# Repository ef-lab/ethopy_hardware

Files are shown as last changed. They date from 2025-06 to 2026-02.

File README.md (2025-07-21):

# 🏠 Hardware for EthoPy

Welcome to the **Hardware for EthoPy** repository! This collection includes all hardware information required to build the setups described in EthoPy. 

## 📦 What's Inside

This repo includes one folder for each behavioral system supported by EthoPy with the:
- **Instructions** – step-by-step guides to build this setup and parts list 
<!-- - **Parts list** – all hardware components required -->
- **3d_designs** – ready-to-print `.stl` files 

## 📁 File Structure

```bash
├── README.md
├── Homecage/
│   └── README.md
│   └── Instructions.pdf
│   └── 3d_designs      
│       └── base.stl
│       └── screen_holder.stl
│       └── ...
├── Openfield/
│   └── ...
├── Air-track/
│   └── ...
```

<!-- ## 📸 Gallery

_Add screenshots or photos of the final printed setup here!_ -->

## 🛠️ Modifications & Contributions

Want to tweak a design? Feel free to fork the repo and customize. PRs are welcome if you want to contribute new variations or improvements!

## 📜 License

This project is licensed under the **MIT License** – see the [LICENSE](./LICENSE) file for details.

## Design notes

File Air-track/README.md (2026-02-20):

# Air-track setup

In this paradigm, head-fixed mice perform a visual two-alternative forced choice task. This setup can be adapted to accommodate more sensory modalities by using appropriate equipment.

<p align="center">
  
</p>

## Hardware Parts List

### Electronics

| # | Item | Qty | Source | Identifier | Ind. Price | Notes |
|:-:|:-:|:-:|:-:|:-:|:-:|:-:|

| 1 | Bpod port interface board | 3 | Sanworks | 1008 | 33€ |Controlling the behavior ports | 

| 2 | solenoid valves | 2 | LEE | LHDA0533415H | 92.81€ | |

| 3 | Infrared Emitter 880nm Circular Right Angle 2-Pin Side Looker | 3 | Honeywell | SEP8736-002 | 4.75€ |For the behavior ports |

| 4 | Phototransistor IR Chip Silicon 880nm 2-Pin Side Looker | 3 | Honeywell | SDP8436-002 | 1,31€ | For the behavior ports |

| 5 | Ethernet cable | 3 | Bel | BC-5UK005F | 2.74 € | |

| 6 | Cable 0.05 mm², Ø 0.8mm | 1 | TRU_ | 1567774 | 4.29€ | |

### Other Hardware

| # | Item | Qty | Source | Identifier |  Ind. Price | Notes |
|:-:|:-:|:-:|:-:|:-:|:-:|:-:|

| 1 | Plexiglas air-table | 1 | Provided by Mostafa A. Nashaat, Larkum Lab, Larkum Lab, Charite, Berlin | | | |

| 2 | PLA platform | 1 | Provided by Mostafa A. Nashaat, Larkum Lab, Charite, Berlin | | | |

| 3 | Behavior port | 3 | Sanworks |  | 215€ |

| 4 | Crimp For Dupont Female | 15 | Local Market |  | 0.50€ | |

| 5 | Tygon S3™ E-3603 Tubing (water) Ø Inner 2.38mm, Ø outer 3.97mm | 4 pieces | Optubus | TY2,38ST3,97 | 1,89€/m | |

| 6 | Tygon S3™ E-3603 Tubing (water) Ø Inner 0.79mm, Ø outer 2.38mm | 2 pieces | Optubus | TY0,79ST2,38 | 1,46€ /m | |

| 7 | V-Hive Enclosure Base Model | 1 | RatRig | HW3303GK | 118€ | |

| 8 | Sound insulator ISOLFON foam plate | 4 pieces 50x50cm and 2 pieces 50x43cm | Local Market | | ~3.5€ / 5 sq. m | for sound and light insulation | 

| 9 | Heat shrink set | | GROBOTRONICS | 05-00017098 | 9.90€ | |

### 3D printed parts

You will find the blueprints for the items you should 3D print [here](3d_designs).

| # | Item | Qty | Filename |
|:-:|:-:|:-:|:-:|
| 1 | screen holders | 2 | [screen_holder.stl](3d_designs/screen_holder.stl) |

## Step-by-step Assembly instructions

You will find the blueprints for the items you should 3D print [here](3d_designs).

> **Info:** The  air-table ([see Other Hardware, part #1](#hardware1)) and platform ([see Other Hardware, part #2](#hardware2)) of the air-track were developed by Dr. Mostafa A. Nashat and assembly (https://doi.org/10.1152/jn.00088.2016, https://doi.org/10.1101/2024.08.22.608577).

**Step 1**. Set up the [Raspberry Pi Behavioral Setup](../Homecage/README.md) following steps 1-7, modifying Raspberry Pi Behavioral Setup Step 5 to connect only the valves ([see Electronics, part #2](#electro2)) to the EthoPy Controller Board.

**Step 2**. Mount the Raspberry Pi Behavioral Setup on the screen holders ([see 3D printed parts, part #1](#printed1)) in front of the air-table (Fig. 1).

<p align="center">
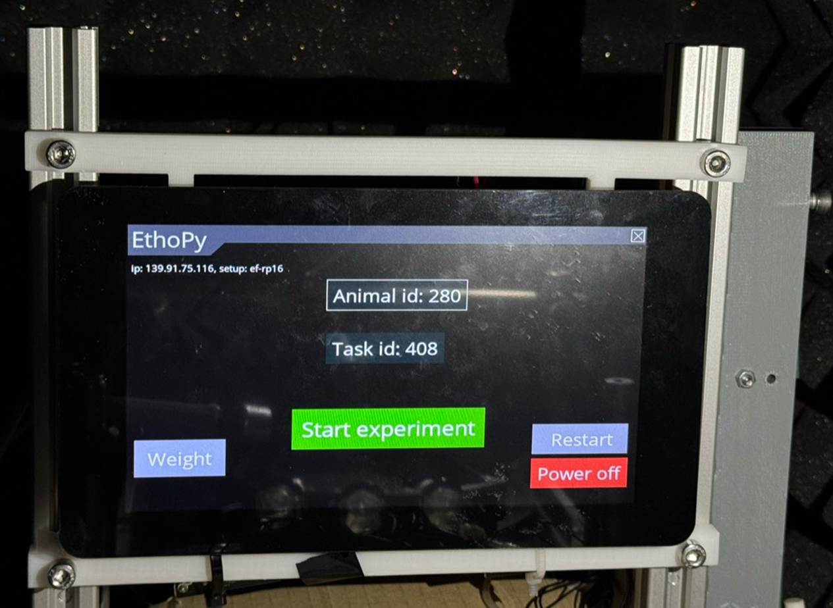
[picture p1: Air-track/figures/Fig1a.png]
  
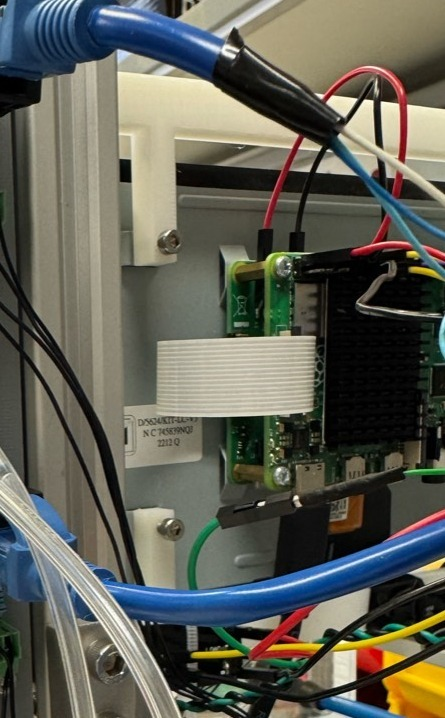
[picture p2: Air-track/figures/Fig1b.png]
  
  <br>
  <em>Figure 1: The RP behavioral setup, mounted on the aluminum rails of the air-table using the screen holders.</em>
</p>

**Step 3**. Assembling of a behavior port ([see Other Hardware, part #3](#hardware3)). Mounting of the infrared emitter ([see Electronics, part #3](#electro3)) and phototransistor ([see Electronics, part #4](#electro4)) to the port was performed following the instructions provided [here](https://sanworks.github.io/Bpod_Wiki/assembly/mouse-behavior-port-assembly/). Each platform included three behavior ports.

> **Note:** For our experiments, we did not include LED light in the behavior ports.

**Step 4**. Set up three Bpod port interface boards ([see Electronics, part #1](#electro1)) as per instructions provided [here](https://sanworks.github.io/Bpod_Wiki/assembly/port-breakout-board-assembly/). Place the Bpod port Interface Boards close to the Air-track and the Raspberry Pi Behavioral Setup for convenience.

**Step  5**. For each port, connect the infrared emitter and phototransistor with the Bpod port interface board.

> **Note:** To reduce the tension caused to the platform from these connections, prefer using wires with a cross-section of 0.05 mm² and an outer diameter of 0.8 mm ([see Electronics, part #6](#electro6)).

**Step 6**. Connecting the Bpod port interface boards to the Raspberry Pi Behavioral Setup. As the connections with the Bpod port interface board are through an Ethernet cable, you will need 3 Ethernet cables, one per port ([see Electronics, part #5](#electro5)).

**Step 7**. Remove the insulation from the edge of the Ethernet wires. Place 13 female terminals ([see Other Hardware, part #4](#hardware4)) at the end of each wire and cover the exposed terminal with insulation (e.g., heat shrink tube, [see Other Hardware, part #9](#hardware9)). In the following steps, the identification of the Ethernet cable wires is shown in (Fig. 2).

<p align="center">
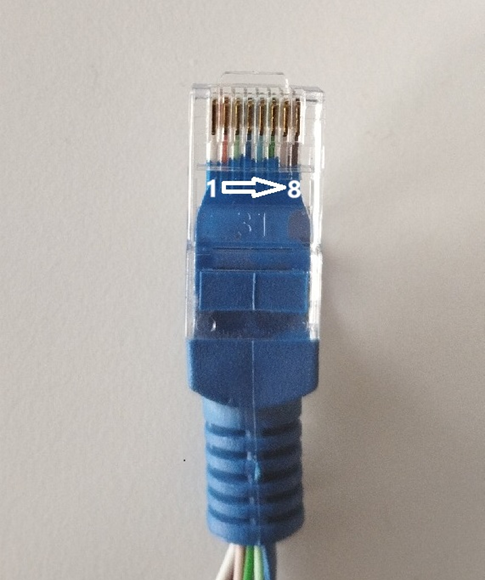
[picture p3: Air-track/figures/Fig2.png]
  
  <br>
  <em>Figure 2: Ethernet cable wire number ids.</em>
</p>

> **Note:** You will use the wires 1 (signal of the sensor), 4 (power of the emitter), 5 (ground).

**Step 8**.  The wires from the Ethernet cables are connected to the Raspberry Pi Behavioral Setup (see GPIO connections as set in [EthoPy documentation](https://ef-lab.github.io/ethopy_package/local_conf/?h=channel#4-schema-names-optional)) as follows:

- Connect `wire 1` (signal) of each Ethernet cable to the <ins>respective GPIO pin</ins> for the proximity input of each port.
- Connect `wire 4` (power) of each Ethernet cable to a <ins>5V power pin</ins>.
- Connect `wire 5` (ground) of each Ethernet cable to a <ins>ground pin</ins>.

> **Note:**  Power cables and grounds should be short-circuited together to connect to one pin of the Raspberry Pi.

**Step 9**. Driving of the valves for ports 1 and 2 using the [EthoPy Controller Board](../EthoPy_Controller/README.md).

**Step 10**. Adjust the reward tubes ([see Other Hardware, part #5](#hardware5), [part #6](#hardware6)) to the behavioral port and connect the valves. Bridge the valves and connect to the water supply (Fig. 3).

<p align="center">
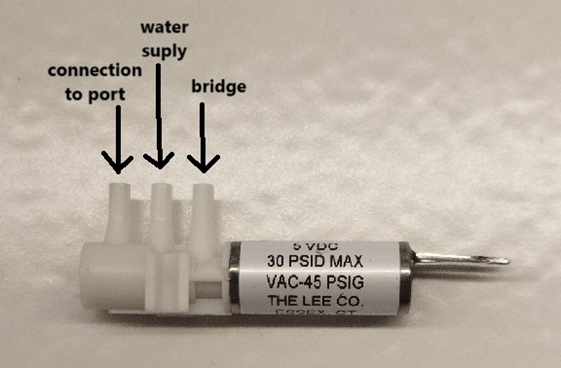
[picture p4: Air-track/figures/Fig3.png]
  
  <br>
  <em>Figure 3: Solenoid valve with the positions of the tubes</em>
</p>

**Step 11**. If sound/light insulation is needed, the Air-track behavioral system can be enclosed in the [Rat-Rig V-Hive Enclosure Base Model](https://ratrig.dozuki.com/Guide/01.+V-Hive+Enclosure+Base+Model/183?lang=en) ([see Other Hardware, part #7](#hardware7)). For further sound and light insulation, related insulation material (e.g. ISOLFON foam plate, see ([see Other Hardware, part #8](#hardware8))) can be used to cover the sides of the enclosure.

**Step 12**. The behavioral system should be placed in a room with air supply, needed for the floating of the platform on the air-table and the water delivery.

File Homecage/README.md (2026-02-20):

# Raspberry Pi Behavioral Setup
A key component of multiple Ethopy behavioral systems is the [Raspberry Pi](https://www.raspberrypi.com/), a small, affordable, single-board computer. It includes ports for HDMI, USB, Ethernet, audio, camera interface (CSI), display interface (DSI), and General Purpose Input/Output (GPIO) pins. It primarily runs on a Linux-based OS called Raspberry Pi OS, and also supports other operating systems. Below, we analytically describe the steps to implement a Raspberry Pi-based behavioral setup.

<p align="center">
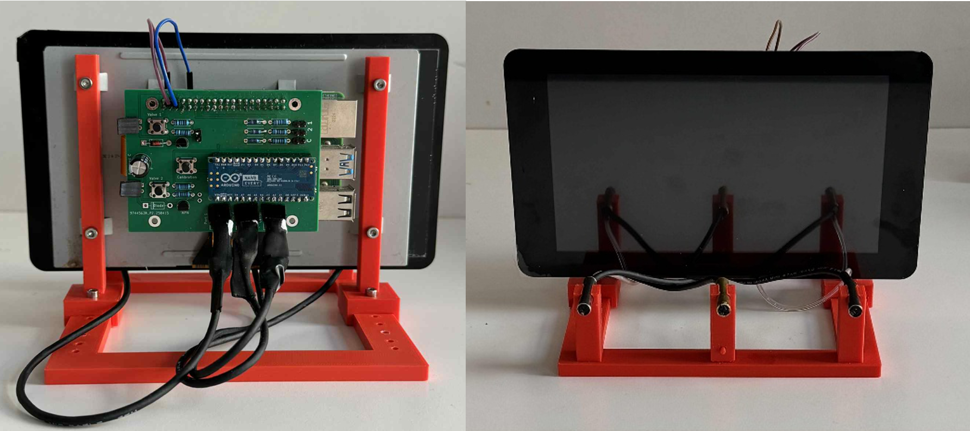
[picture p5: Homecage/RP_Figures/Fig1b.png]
  
</p>

## Hardware Parts List

### Electronics

| # | Item       | Qty     | Source           | Identifier        | Ind. Price | Notes              |
|:-:|:-:  |:-:      |:-:  |:-:    |:-:   | :-:        |

| 1 | Raspberry Pi 4 Model B/4GB                    | 1       | Raspberry Pi             |SC0192-3|  55€  |  |

| 2 | Official Raspberry Pi 7 Touch Screen Display  | 1       | Raspberry Pi              |  2473872         |  75€  | |

| 3 | Premium High Speed microSD Card               | 1       |  Integral  | INMSDH32G-100/70V30              |   6.73€   | |

| 4 | EthoPy Controller Board                       | 1       | [Custom](../EthoPy_Controller/README.md)  |      |     |  |

| 5 | Lick Ports                                    | 2 or 3  | [Custom](Lick_ports_assembly.md)   |          |    | 2 to detect licks and deliver water, 1 can be used as a proximity indicator (center port) |

| 6 | Beam Photoelectric Sensor      | 1    | HAITRONIC         | HR0172    |  2€ |Can be used as a proximity indicator (center port)                                         |

| 7 | Solenoid valves            | 2       | LEE SLR         | LHDA0533415H         |     95€   | |

| 8 | Ultrasound Speakers 40kHz     | 2       | PUI Audio      | UT-1640K-TT-2-R| 3.20€    |For auditory experiments. See: [Speakers_assembly](Speakers_assembly.md)             |

### Other Hardware

| # | Item                                | Qty | Source      | Identifier    | Ind. Price | Notes       |
|:-:|:-:                                  |:-:  |:-:          |:-:            |:-:          | :-:          |

| 1 | M3 screws                           | 6   | Grobotronics  | M3X12/D7985  |     1.80€    |    |

| 2 | Raspberry Pi 4 Heatsink (40x30x5mm) | 1   | Grobotronics  | 49-00012076  |   1.80€ |    |

### 3D Printed Parts
You will find the blueprints for the items you should 3D print [here](3d_designs).
| # | Item                          | Qty | Filename                                                                                            | Notes                           |
|:-:|:-:                            |:-:  |:-:                                                                                                  |:-:                              |
| 1 | Base                          | 1   | [base.stl](3d_designs/base.stl)                                            | Includes the lick port holders  |
| 2 | Screen holder                 | 2   | [screen_holder.stl](3d_designs/screen_holder.stl)                          |                                 |
| 3 | Center port holder            | 1   | [center_port.stl](3d_designs/center_port.stl)                              |                                 |
| 4 | Center port & speaker holder  | 1   | [center_port_with_speakers.stl](3d_designs/center_port_with_speakers.stl)  | Includes speaker holders        |
| 5 | Pins                          | 1   | [pin.stl](3d_designs/pin.stl)                                              | For mounting the center port holder |

<p align="center">
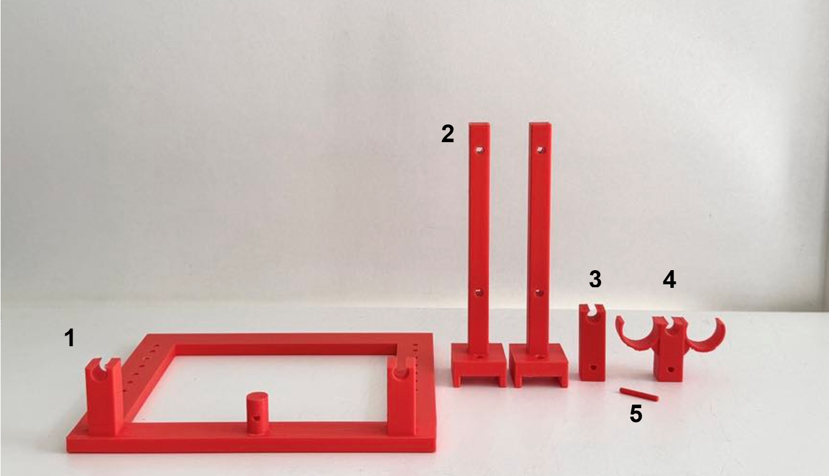
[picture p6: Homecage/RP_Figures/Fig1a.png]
  
  
  <br>
  <em>Figure 1: RP setup (top: 3D printed parts of the RP's base, bottom: assembled RP base).</em>
</p>

## Step-by-step Assembly Instructions

**Step 1**. Install the [operating system of the RPi](https://www.raspberrypi.com/documentation/computers/getting-started.html#installing-the-operating-system). In our experiments, we have used the [Bullseye Raspberry Pi OS](https://www.raspberrypi.com/news/raspberry-pi-os-debian-bullseye/).

**Step 2**. Mount the Raspberry Pi to the Raspberry Pi Touch Display and connect the Flat Flexible Cable and the power of the Touch Display to the Raspberry Pi [instructions](https://www.raspberrypi.com/documentation/accessories/display.html).

**Step 3**. Connect the Ethopy Controller Board to the RPi.

**Step 4**. Add a heatsink ([Other Hardware parts list, item #2](#other2)) on the back of the RP to avoid excessive warming.

**Step 5**. Plug in the side and the center ([lick](Lick_ports_assembly.md) or interruptor) ports, and the valves to the EthoPy Controller Board, to the positions indicated on the board.

**Step 6**. Connect the valves to the water supply. Each LEE valve ([Electronics parts list, item #7](#electro7)) has 3 pipe-edges (1) to be connected to the lick port tube, (2) to be connected with the water supply tube, and (3) to be connected with the other valve through a tube and 2 pins to be connected to the board (Fig. 2, left).

In the RP setup, the upper valve corresponds to the left lick port, and the bottom valve corresponds to the right lick port (Fig. 2, right).

<p align="center">
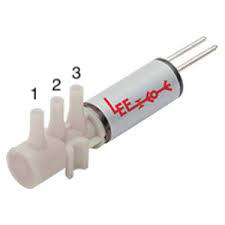
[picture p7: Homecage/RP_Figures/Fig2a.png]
  
  
  <br>
  <em>Figure 2: Connections of the solenoid valve (left: positions of the tubes, right: placement of the valves on the RP board).</em>
</p>

**Step 7**. Connect to the RPi and run a test task.

- ssh username@ip_address 

> For more information, visit their: [Rasberry Pi: Remote access](https://www.raspberrypi.com/documentation/computers/remote-access.html)

- Follow the instructions on how to [install/run EthoPy](https://ef-lab.github.io/ethopy_package/installation.html)

> **Note (Optional):** Rename the RP and set a static IP address.

> **Tip:** When using multiple RPs, it is best to use unique names that follow a consistent structure and assign static IP addresses to each RP to facilitate identification and management. To do this, connect to the RP and change its default name following the [instructions](https://ef-lab.github.io/ethopy_package/raspberry_pi). It is recommended to use a fixed prefix followed by an incremental number for each RP added.

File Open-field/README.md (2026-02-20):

# Open-field Behavioral Setup Instructions

In this protocol, the open-field behavioral setup is used to allow freely-moving mice to perform two-alternative forced choice tasks. Below, we describe the protocol to implement an open-field behavioral setup for  a visual discrimination task.

## Hardware Parts List

### Electronics

| # | Item                               | Qty | Source                 | Identifier       | Ind. Price  | Notes            |
|:-:|:-:                                 |:-:  |:-:                     |:-:               |:-:          |:-:        |

| 1 | Arduino Nano Every Board           | 1   | Arduino Store          | ABX00028     |     14.5€    | |

| 2 | PCB Controller Board               | 1   | JLCPCB (JiaLiChuang (HongKong) Co., LTD) | [custom](../EthoPy_Controller/README.md)| 1.4€ | |

| 3 | 13.3" Capacitive Touch Screen LCD  | 1   | Waveshare                                | HDMI LCD (H)     |  144€   | Presentation of stimuli, with Toughened Glass Cover, 1920×1080 |

| 4 | HDMI Cable (2m, 4K/60Hz)           | 1   | Ugreen                   |     ED015   | 11.90€ |Connects the screen with the PC                    |

### Other Hardware

| # | Item       | Qty | Source       | Identifier  | Ind. Price    | Notes          |
|:-:|:-:         |:-:  |:-:           |:-:          |:-:            |:-:              |

| 1 | V-SLOT 2020 1500mm         | 1   | Grobotronics | 27-99920208      |  14.80€      | cut into 4 pieces of 31 cm length                    |

| 2 | V-SLOT 2020 250mm         | 4   | Grobotronics | 27-99920210      |   2.5€    |        |

| 3 | V-SLOT 2020 500mm    | 2   | Grobotronics | 27-99920209         |     4.9€     |                        |

| 4 | Inside Hidden Corner Bracket 3-Way        | 4   | Grobotronics | 14-00015421           |        1.6€      |           |

| 5 | RatRig Cast - 90 Degree Corner Bracket    | 4   | Grobotronics | 27-22280012            |    0.6€    |       |

| 6 | Plexiglass Plates     | 7   | Local vendor |         |  2€ | 2 33x33cm plates, 1 30x30cm plate, 4 35x30cm plates  |

| 7 | V-Hive Enclosure Base Model     | 1   | RatRig       | HW3303GK        |   118€     | Insulation of light and sound                        |

| 8 | ISOLFON Foam Plate      |    | Local Market    |       |  ~3.5€ / 5 sq. m | Sound insulator               |

| 9 | M4 Screws       |    | Local Market        |          | ~0,30€ | 11x L10 & 16x L8                                     |

| 10| M4 T-nuts 20x20          | 9   | Local Market       |                 |  0,20€  |       | 

| 11| V-Slot Gantry Set 2020 with Three Wheels  | 2   | Grobotronics | 14-00020155           |    9.90€     |                    |

| 12| Lickport                | 1   |             | [Custom](../Homecage/Lick_ports_assembly.md) |         |     Delivers water       |

| 13| LHD Series 3-Way Control Solenoid Valve   | 1   | Lee SLR      | LHDA0533415H           |    95€   |        |

### 3D Printed Parts

You will find the blueprints for the items you should 3D print [here](3d_designs).

| # | Item            | Qty | Filename                                                                                              | Notes |
|:-:|:-:              |:-:  |:-:                                                                                                    |:-:    |
| 1 | Lower Corners   | 4   | [open-field_bottom_corner.stl](3d_designs/open-field_bottom_corner.stl)    |       |
| 2 | Upper Corners   | 4   | [open-field_top_corner.stl](3d_designs/open-field_top_corner.stl)          |       |

## Step-by-step Assembly Instructions

The open-field behavioral setup is enclosed in the Rat-Rig V-Hive Enclosure Base Model ([Other Hardware list, item #7](#other7)). Assembly instructions can be found here.

### Enclosure & Sound Insulation

**Step 1**. To make the enclosure sound-proof, use sound insulation material (eg. ISOLFON foam plate, ([Other Hardware list, item #8](#other8))) to cover all sides of the enclosure, i.e. use 4 pieces with dimensions 50x50cm and 2 pieces with dimensions 50x43cm.

### Arena Construction

The interior of the enclosure consists of a plexiglass box (arena), where the mouse is placed during the experiment (base: 30x30cm, walls: 35x30 cm, ([Other Hardware list, item #6](#other6))).

**Step 2**. Glue (e.g. hot glue) each side of the arena and place 3D printed parts (3D printed parts list, items #1,2) on the upper and lower corners (Fig. 1).

<p align="center">
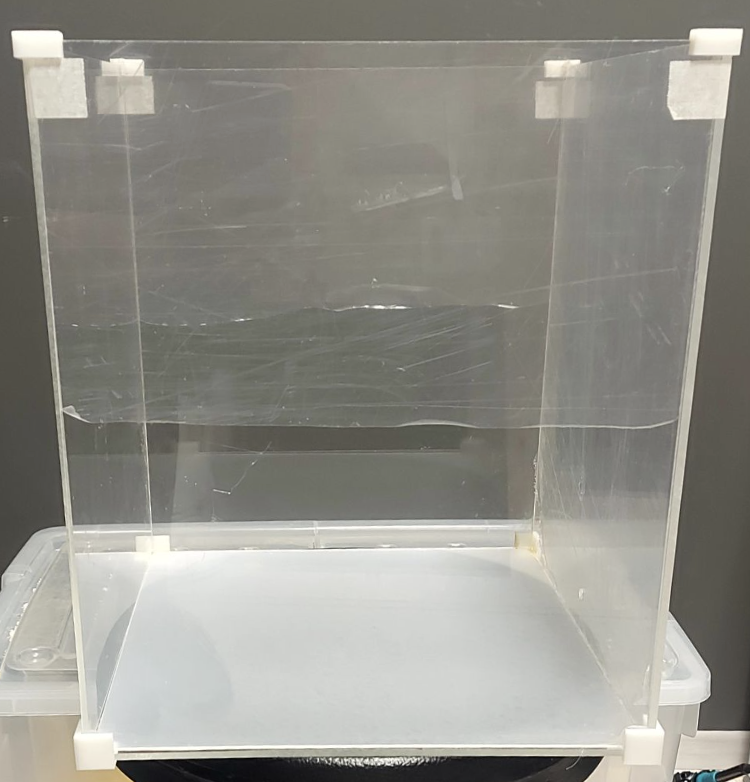
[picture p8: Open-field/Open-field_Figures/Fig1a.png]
  
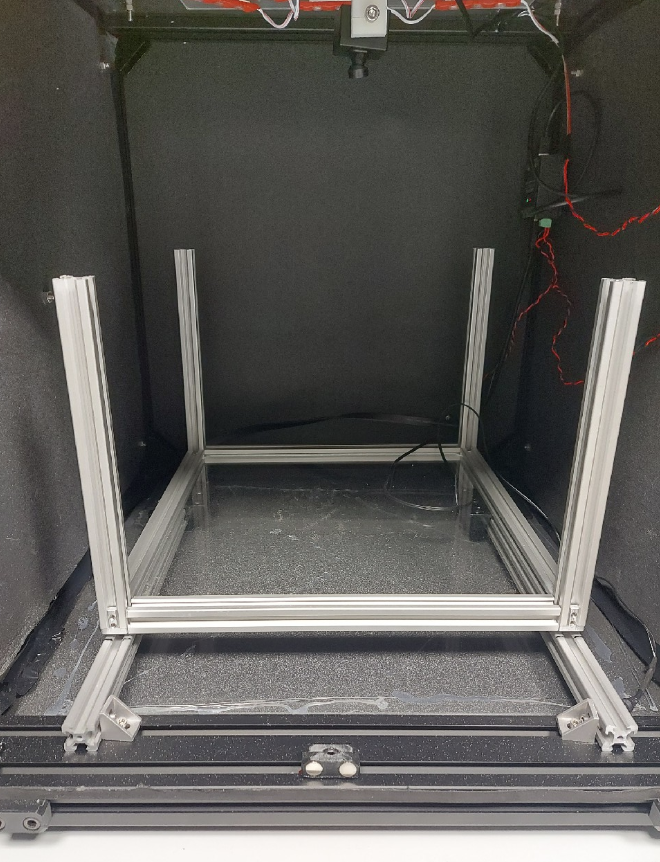
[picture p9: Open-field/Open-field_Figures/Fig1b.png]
  
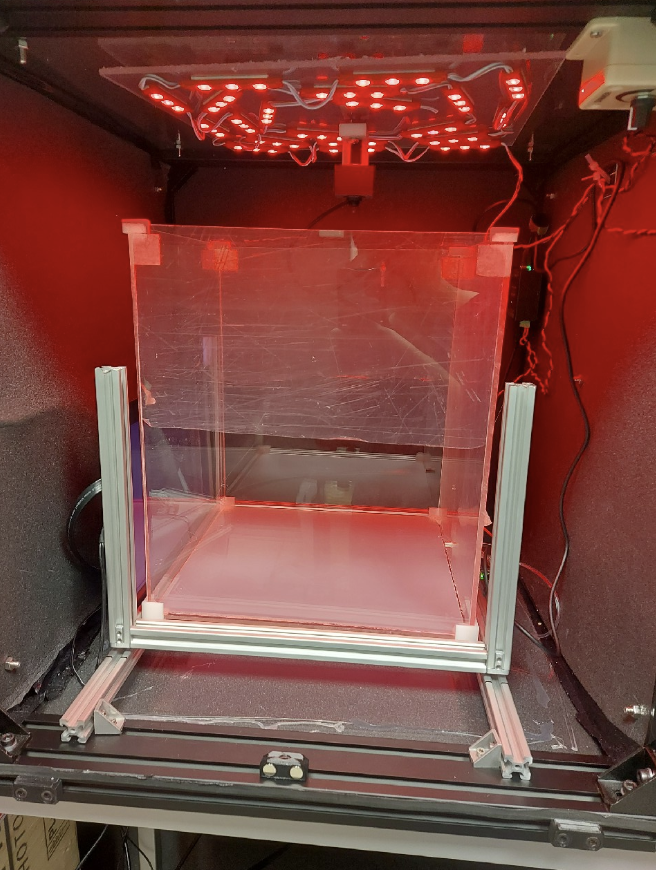
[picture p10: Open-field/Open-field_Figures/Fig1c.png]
  
  <br>
  <em>Figure 1: Open-field arena: the arena (left), the base of the arena (center) and the arena on top of its base and inside the enclosure (right) </em>
</p>

**Step 3**. Construct the following drawer to place the arena (Fig. 1).

- `Base`: 4 V-SLOT 2020 ([Other Hardware list, item #1](#other1)) with a length of 31 cm each. Connect the rails in the shape of a square and place a plexiglass (33x33cm, Other Hardware list, item #6) in the middle. When connecting the plexiglass to the square, you need to cut its corners at around 6.1 mm.

- `Columns`: 4 V-SLOT 2020 250 mm ([Other Hardware list, item #2](#other2)). Connect them on the base.

- For the `connections` of the base and columns, use Inside Hidden Corner Brackets and M4 (8mm) screws ([Other Hardware list, item #4,9](#other4,9)).

- `Rails`: 2 V-SLOT 2020 with a length of 50 cm each ([Other Hardware list, item #3](#other3)). Place the rails on the base of the box and screw them using 4 90-Degree Corner Brackets ([Other Hardware list, item #5](#other5)). To screw the brackets on the V-SLOTS, use M4 screws (10mm, ([Other Hardware list, item #9](#other9))) and M4 20x20 Tee Nuts (Other Hardware list, item #10).

- `Sliding`: Screw 2 V-Slot Gantry Sets 2020 with Three Wheels ([Other Hardware list, item #11](#other11)) on each side of the base with M4 (8mm, ([Other Hardware list, item #9](#other9))) screws and M4 20x20 Tee Nuts ([Other Hardware list, item #10](#other10)). Attach each V-Slot Gantry Set to the rails.

### Screen

**Step 4**. Place a screen ([Electronics list, item #3](#electro3)) on the one side of the box between the 2 V-slots (Fig. 2).

**Step 5**. Connect the cable for power (included in the 13.3inch Capacitive Touch Screen LCD, ([Electronics list, item #3](#electro3))) and the HDMI ([Electronics list, item #4](#electro4)) (Fig. 1).

<p align="center">
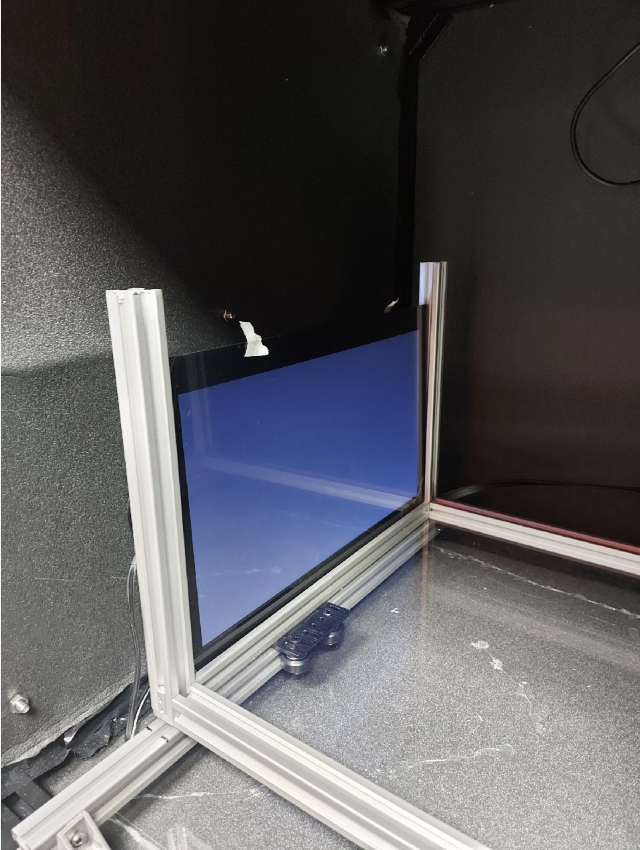
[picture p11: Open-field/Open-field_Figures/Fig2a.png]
  
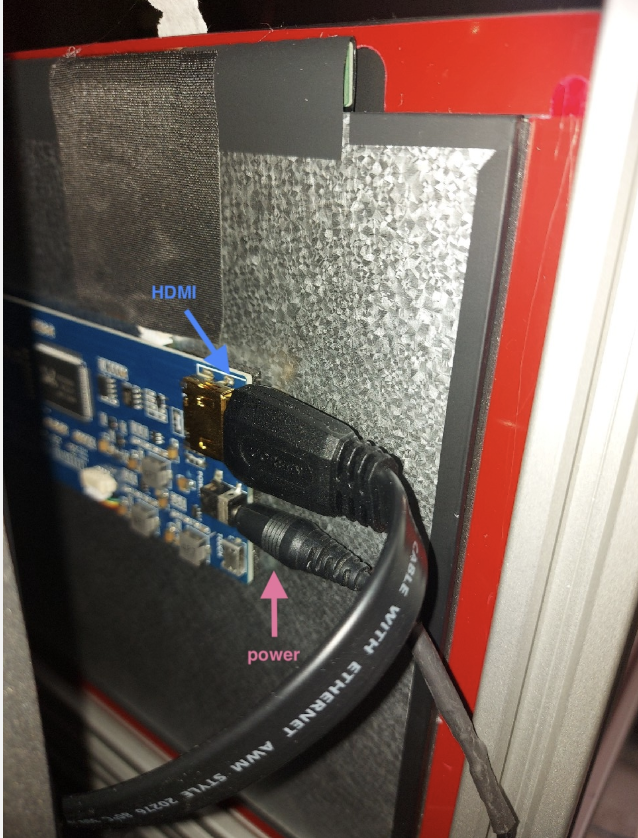
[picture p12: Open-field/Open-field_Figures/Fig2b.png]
  
  <br>
  <em>Figure 2: Screen: front side of the screen (left) and back side of the screen and connections (right)</em>
</p>

### Arduino Board

**Step 6**. Follow instructions for [EthoPy Controller Board](../EthoPy_Controller/README.md)

### Lickport

**Step 7**. Follow instructions [here](../Homecage/Lick_ports_assembly.md) to make the lickport ([Other Hardware list, item #12](#other12)).

**Step 8**. Connect the lickport to the arduino board and a solenoid valve ([Other Hardware list, item #13](#other13)) in a pressurized tubing network (STAR methods, liquid delivery).

### Extra Parts

To record the experiment you will aslo need red LED lights and a camera capable of recording fps>30 and a fov>80&deg; (We used Arducam 2.3MP AR0234 Color Global Shutter USB 3.0)

### PC Requirements
For the Open-field setup in the EthoPy project, in addition to the standard installation, you will need to enable real-time pose estimation by installing `DeepLabCut-Live`, which provides a lightweight, low-latency inference pipeline for online tracking. To achieve frame rates greater than 30 FPS, we strongly recommend using a system running Ubuntu paired with a powerful NVIDIA GPU (minimum 8GB VRAM), as this ensures compatibility with TensorFlow and allows for GPU-accelerated inference. CPU-only systems or unsupported GPUs (e.g., Intel or AMD) will not meet the real-time demands.

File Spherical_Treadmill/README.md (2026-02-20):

# Spherical Treadmill Behavioral Setup

The Spherical Treadmill (ball) behavioral setup is used for head-fixed mice performing sensory navigation tasks (e.g., olfactory, visual, multimodal). Below, we describe the protocol to construct an odor-based virtual reality setup.

<p align="center">
  
</p>

## Hardware Parts List

### Electronics

| # | Item        | Qty  | Source      | Identifier  | Ind. Price |  Notes                                 |
|:-:|:-:          |:-:   |:-:          |:-:          |:-:         |:-:                                     |

| 1 | solenoid valves        | 5    | fspumb.cn       | 0526T    |   9€  | 4 for odorants, 1 for water delivery   |

| 2 |MOSFET board               | 5    | OEM             | FR120N   |  0.50€   | To control the solenoid valves         |

| 3 | Capacitive sensor board   | 1    | Sparkfun        | AT42QT1011  |  7.35€ | for lick detection                     |

| 4 | laser mouse               | 2    | DELL            | MS3220    |   27.87€  | ball sensors                           |

### Other Hardware

| # | Item                      | Qty  | Source          | Identifier  | Ind. Price |  Notes                                 |
|:-:|:-:                        |:-:   |:-:              |:-:        |:-   |:-:                                     |

| 1 | ball bearings             | 3    | DFRobot         | FIT0007   | 2.19€   |                                        |

| 2 | plastic box               | 1    | Kradex          | Z74HJ      | 6€  | 30 x 20 x 10cm                         |

### 3D Printed Parts

You will find the blueprints for the items you should 3D print [here](3d_designs).

| # | Item                  | Qty | Filename                                                                        | Notes             |
|:-:|:-:                    |:-:  |:-:                                                                              |:-:                |

| 1 | mouse post            | 2   | [mouse_post.stl](3d_designs/mouse_post.stl)                 |                   |

| 2 | ball bearing holder   | 3   | [ball_bearing_holder.stl](3d_designs/ball-bearing-post.stl) |                   |

| 3 | 5-way tube connector  | 1   | [tube_connector.stl](3d_designs/tube_connector.stl)         |                   |

## Step-by-Step Assembly Instructions

Following instructions apply for any virtual reality system that uses a styrofoam ball on 3 ball bearings (similar to Fig. 4d of the EthoPy paper) <!--Add hyperlink-->, 4 odours to define an olfactory virtual environment, and a mouthpiece to deliver the odors but also the reward.

**Step 1**. Set up the [Raspberry Pi Behavioral Setup](../Homecage/README.md) following steps 1-5, the difference is that in this setup you need 5 valves ([Electronics parts list, item #1](#electro1)), for reward and 4 for odour delivery.

**Step 2**. A `Styrofoam ball` is supported by three (3) metallic ball bearings ([Other Hardware parts list, item #1](#other1)) allowing smooth navigation for prolonged periods. The bearings are supported by custom 3D-printed posts ([3D-printed parts, part #2](#printer2)) at a 45° angle, so the ball is stable while the subject is performing the task.

<p align="center">
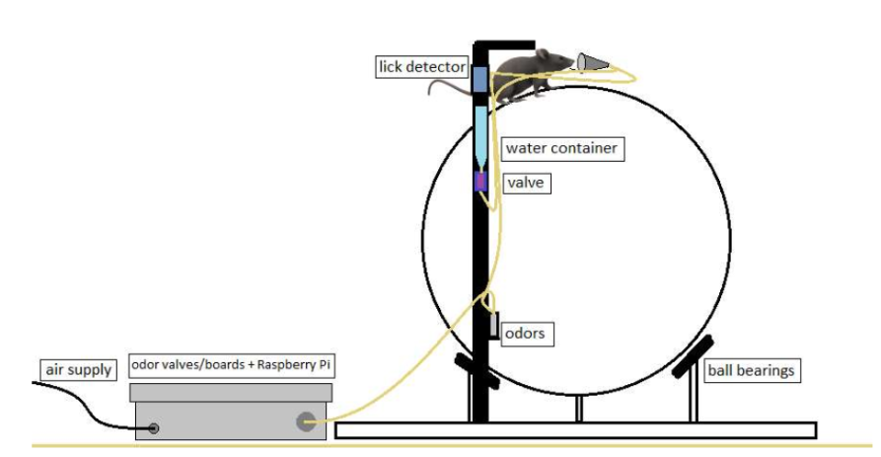
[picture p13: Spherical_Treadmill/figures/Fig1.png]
  
  <br>
  <em>Figure 1: Animated depiction of the experimental set-up. Mouse is head-fixed onto a styrofoam ball, with a mouthpiece securing the odor and water delivery.</em>
</p>

**Step 3**. The PCB boards of the laser mice ([Electronics parts list, item #4](#electro4)) are used as sensors to encode the ball movement. Laser mice holders ([3D-printed parts, part #1](#printer1)) are used to place the laser mice in an optimal position at 90⁰ degrees from each other, very close to the bearings, and at an incline of 55°, to eliminate the distance variation between the ball and the sensor that could lead to imprecise tracking information. Insert the PCB board of each laser mouse and ensure they have 2-3 mm distance from the surface of the ball (Fig. 2).

<p align="center">
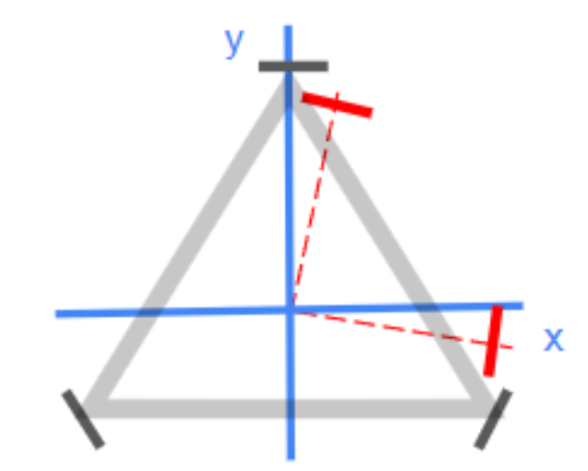
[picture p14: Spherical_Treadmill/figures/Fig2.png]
  
  <br>
  <em>Figure 2: Schematic of the locations of the ball bearing holders (grey) and the laser mice (red).</em>
</p>

> **Note:** Details about the how EthoPy computes the distances covered by the animal are in [`vr_ball_readme.md`](https://github.com/ef-lab/ethopy_plugins/blob/main/spherical_treadmill/behaviors/vr_ball_readme.md)

**Step 4**. The odor and water delivery system requires constant air supply and 5 solenoid valves. The air supply is connected to a 5-way manifold ([3D-printed parts, part #3](#printer3)) with the 4 valves that open and close when a pulse is sent from the RP through the MOSFET ([Electronics parts list, item #2](#electro2)). Upon pulse delivery the valves open for the specified duration and the air travels through the odor bottle to the mouthpiece. Similarly for the water supply, water is delivered to the lick port inside the mouthpiece upon correct response. 

> **Note:** Odors are released depending on the animal's virtual location and are calculated in [`EthoPy Ball`](https://github.com/ef-lab/ethopy_plugins/blob/main/spherical_treadmill/stimuli/vr_odors_readme.md) 

<p align="center">
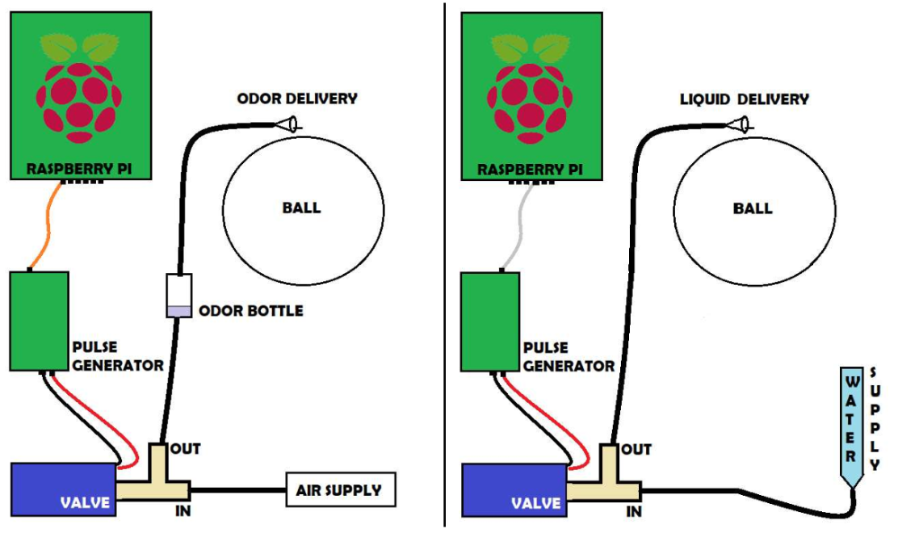
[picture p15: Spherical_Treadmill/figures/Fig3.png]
  
  <br>
  <em>Figure 3: Animated depiction of the assembly of the stimuli that arrive at the mouthpiece odors (left) and water (right). </em>
</p>

### Electrical Connections

- `Valves’ control circuit`: To control the valves, we use a MOSFET board ([Electronics parts list, item #2](#electro2)) and connect the power and ground of the valve to the board, placing the power at position 2a and the ground at position 2b shown in [Fig. 4](#fig4). Then, to connect it with the Raspberry Pi, we select the pin of the RP we have programmed to trigger the valve and a ground pin and connect the other end to the PWR and GND pins respectively placed at the top part of the board (position 3, (Fig. 4)). Lastly, to turn on the board we need to insert 2 cables at position 1, one for the power and one for the ground of the power supply. In this last step, it is advised to make a 6-way cable assembly, both for the power and the ground, 5 of them going to each MOSFET board, and one connecting the power supply. This assembly can be placed in a plastic box ([Other Hardware parts list, item #2](#other2)).

<p align="center">
  
  
  <br>
  <em>Figure 4: MOSFET boards for controlling the valves for the odorants </em>
</p>

- `Lick detector circuit`: The Capacitive sensor board ([Electronics parts list, item #3](#electro3)) consists of five pins: GND for ground, OUT for signal, VDD for power supply (1.8V - 5V), LED and PAD (Fig. 5). In this case, only four of the pins are required (GND, OUT, VDD, and PAD). To connect the sensor for the lick detection it is important to solder a trimmed and polished 18G needle to the wire that will connect with the PAD pin. 

<p align="center">
  
  
  
  <br>
  <em>Figure 5: Capacitive Touch Breakout board and Mouthpiece</em>
</p>

- `Laser mice`: Connect the laser mice to the two USB ports of the RP (each USB port will be assigned later in EthoPy code (Interfaces/Ball.py) to determine which laser mouse is responsible for decoding which axes)

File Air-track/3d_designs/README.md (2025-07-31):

# 🖨️ 3D Designs for EthoPy Hardware

This folder contains 3D-printable `.stl` files for components used in the adapted Air-track to be used with EthoPy.

## 📦 Included Models
 
- `screen_holder.stl` – Stand for screen placement

All models are designed for ease of printing and assembly, with minimal support requirements.

## 🖨️ Recommended Print Settings

<!-- - **Layer Height:** `0.2mm`
- **Infill:** `15–25%`
- **Supports:** Not required (unless otherwise noted)
- **Material:** ABS has been tested but PLA, PETG should also work
- **Print Speed:** `50–60 mm/s`
- **Wall Line Count:** `2–3`
- **Top/Bottom Layers:** `4–5` for strength -->

> We use a Zortrax M200 Plus with the Z-ULTRAT material and the default settings and support. However, other FDM printers and ABS, PLA, PETG material should also work. Adjust for your printer as needed.

## 📌 Notes

- Make sure to orient parts flat on the print bed to avoid unnecessary supports.
- All parts can be printed on the current orientation

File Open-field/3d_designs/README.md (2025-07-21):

# 🖨️ 3D Designs for EthoPy Hardware

This folder contains 3D-printable `.stl` files for components used in the EthoPy Openfield setup.

## 📦 Included Models

- `open-field_bottom_corner.stl` – for screen placement
- `open-field_top_corner.stl` – for screen placement
<!--- `lick_port.stl` – Mount for lick detection module
- `screen_stand.stl` – Stand for screen placement
- `speaker_hold.stl` – Bracket for securing a speaker -->

All models are designed for ease of printing and assembly, with minimal support requirements.

## 🖨️ Recommended Print Settings

<!-- - **Layer Height:** `0.2mm`
- **Infill:** `15–25%`
- **Supports:** Not required (unless otherwise noted)
- **Material:** ABS has been tested but PLA, PETG should also work
- **Print Speed:** `50–60 mm/s`
- **Wall Line Count:** `2–3`
- **Top/Bottom Layers:** `4–5` for strength -->

> We use a Zortrax M200 Plus with the Z-ULTRAT material and the default settings and support. However, other FDM printers and ABS, PLA, PETG material should also work. Adjust for your printer as needed.

## 📌 Notes

- Make sure to orient parts flat on the print bed to avoid unnecessary supports.
- All parts can be printed on the current orientation

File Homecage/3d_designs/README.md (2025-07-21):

# 🖨️ 3D Designs for EthoPy Hardware

This folder contains 3D-printable `.stl` files for components used in the EthoPy Homecage setup.

## 📦 Included Models
 
- `base.stl` – Main mounting base
- `center_port.stl` – Center nose-poke port
- `center_port_with_speakers.stl` – Center nose-poke port for the auditory tasks
- `screen_holder.stl` – Stand for screen placement
- `pin.stl` – For mounting the center port holder 

All models are designed for ease of printing and assembly, with minimal support requirements.

## 🖨️ Recommended Print Settings

<!-- - **Layer Height:** `0.2mm`
- **Infill:** `15–25%`
- **Supports:** Not required (unless otherwise noted)
- **Material:** ABS has been tested but PLA, PETG should also work
- **Print Speed:** `50–60 mm/s`
- **Wall Line Count:** `2–3`
- **Top/Bottom Layers:** `4–5` for strength -->

> We use a Zortrax M200 Plus with the Z-ULTRAT material and the default settings and support. However, other FDM printers and ABS, PLA, PETG material should also work. Adjust for your printer as needed.

## 📌 Notes

- Make sure to orient parts flat on the print bed to avoid unnecessary supports.
- All parts can be printed on the current orientation

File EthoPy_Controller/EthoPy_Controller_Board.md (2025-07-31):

# EthoPy Controller Board and Arduino

Arduino is a microcontroller that converts the analog signal from the lick and proximity ports to digital, and a Controller Board ensures the communication between the Arduino and Raspberry Pi.
<div align="center">
<figure id="fig13">
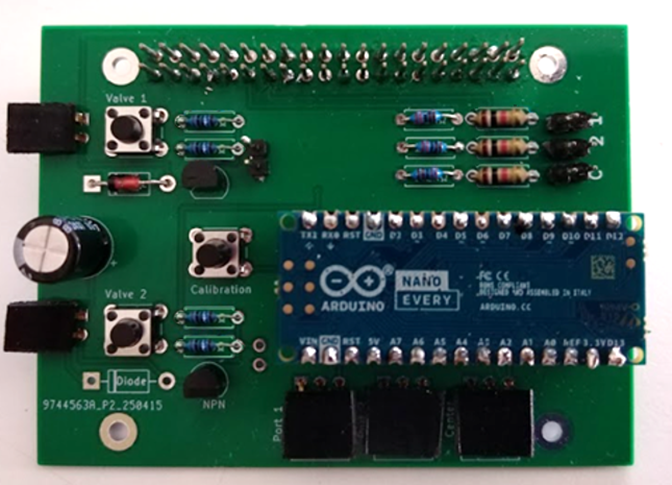
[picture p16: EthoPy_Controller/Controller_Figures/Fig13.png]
  
</figure>
</div>

## 📦 Parts List

### 🔌 Electronics

| # | Item                                      | Qty  | Source                     | Identifier                    | Notes | 
|:-:|:-:                                        |:-:   |:-:                         |:-:                            |:-:    |

| 1 | 40-pin Stackable Female Extra Tall Header | 1    | Grobotronics             |                          |       | <!--Add Mfr. source & Identifier-->

| 2 | Arduino Nano Every                        | 1    | Arduino Store            |                  |       |

| 3 | 1x2 Female Pin Header Right Angle         | 2    | Grobotronics                |05-00011907         |       | <!--Add Mfr. source & Identifier-->

| 3 | 1x3 Female Pin Header Right Angle         | 3    |                 | 05-00011907               |       | <!--Add Mfr. source & Identifier-->

| 4 | 1x2 Male Pin Header                       | 5    |                | 19-00011916                   |       | <!--Add Mfr. source & Identifier-->

| 5 | 1x15 Female Pin Header                    | 2    |                 | 19-00011915                 |       | <!--Add Mfr. source & Identifier-->

| 6 | 1x15 Male Pin Header                      | 2    | Included in Arduino kit    | —                             |       |

| 7 | Metal Film Resistor 100 Ω, 1/4W, 1%       | 4    | YAGEO            | MFR25SFTF52-100R            |       |

| 8 | Metal Film Resistor 2.2 kΩ, 1/2W, 1%      | 3    | YAGEO MFR25SFTF52-2K2            | MFR25SFTF52-2K2           |       |

| 9 | Metal Film Resistor 1 kΩ, 1/2W, 1%        | 3    | YAGEO                | CFR-25JB-1K0           |       |

|10 | Metal Film Resistor 10 kΩ, 1/4W, 1%       | 3    | YAGEO             | CFR25SJT-52-10K            |       |

|11 | BC547B Transistor                         | 2    | onsemi / Fairchild                      | BC547B     |       |

|12 | Aluminium Electrolytic Capacitor          | 1    | Rubycon          | 35ZLR220MEFC8X11.5          |       |

|13 | Tactile Push Button Switch (6×6×6)        | 2    | Same Sky     | TS02-66-70-BK-160-SCR-D     |       |

|13 | Tactile Push Button Switch (6×6×9)        | 1    | —                          |                               | —     | <!--Add Mfr. source & Identifier-->

|14 | Diode Rectifier                           | 2    | Vishay General Semiconductor           | 1N4005-E3/73  |       |

|15 | Printed Circuit Board (PCB)               | 1    | Custom                     | —                             |       |

<figure id="fig1">
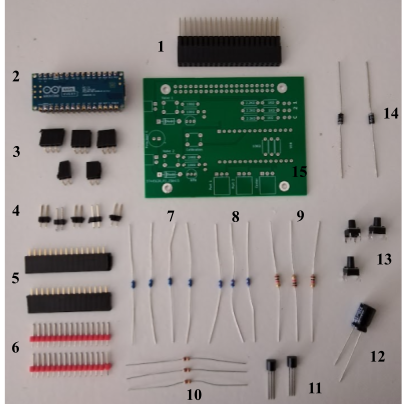
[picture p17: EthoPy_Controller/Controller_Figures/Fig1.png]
  
  <figcaption><b>Figure 1</b>: <i>EthoPy Controller Board and Arduino parts</i></figcaption>
</figure>

> :memo: **Note:** <ins>You will also need</ins>: a soldering iron, a wire cutter

## 🛠️ Step-by-step assemply instructions

**Step 1**. Print the PCB board of the schematic ([Fig. 2](#fig2)). PCB and gerder files for JLPCB are available [here](). <!--Add hyperlink-->

<figure id="fig2">
  
</figure>

**Step 2**. Solder the 1x15 female pin headers on each side of the Arduino Nano Every board ([Fig. 3](#fig3)).

<figure id="fig3">
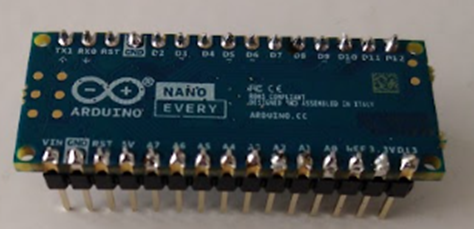
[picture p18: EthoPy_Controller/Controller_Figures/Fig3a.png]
  
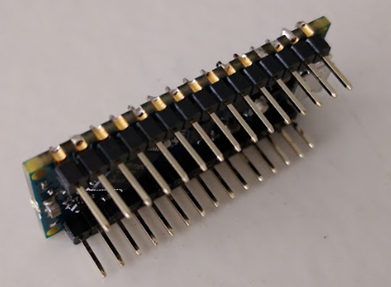
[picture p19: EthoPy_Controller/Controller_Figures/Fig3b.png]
  
</figure>

**Step 3**. Solder each resistor into its designated position on the PCB according to its resistance value ([Fig. 4](#fig4)).

<figure id="fig4">
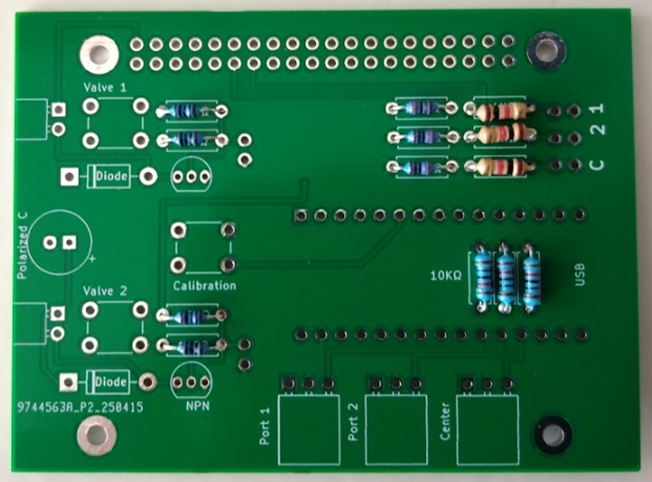
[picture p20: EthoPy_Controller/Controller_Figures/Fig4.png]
  
</figure>

**Step 4**. Solder the five 1x2 male pins headers into the corresponding ports on the PCB ([Fig. 5](#fig5)).

<figure id="fig5">
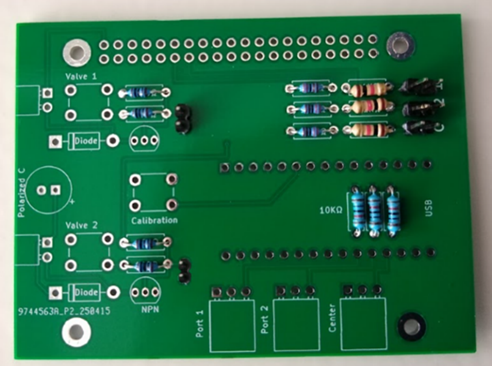
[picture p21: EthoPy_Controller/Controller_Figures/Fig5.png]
  
</figure>

**Step 5**. Solder the transistors onto their correct positions on the board ([Fig. 6](#fig6)).

<figure id="fig6">
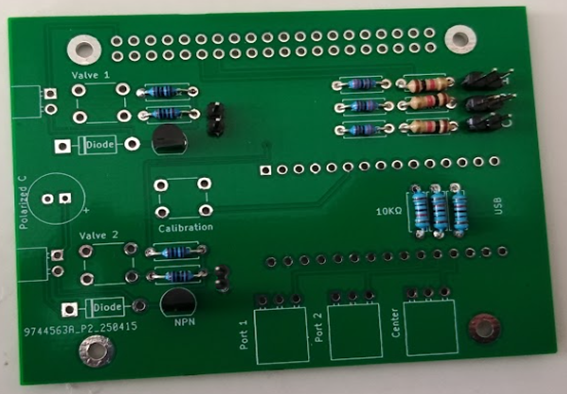
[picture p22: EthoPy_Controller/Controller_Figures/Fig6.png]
  
</figure>

**Step 6**. Solder the diodes in the same way ([Fig. 7](#fig7)).

<figure id="fig7">
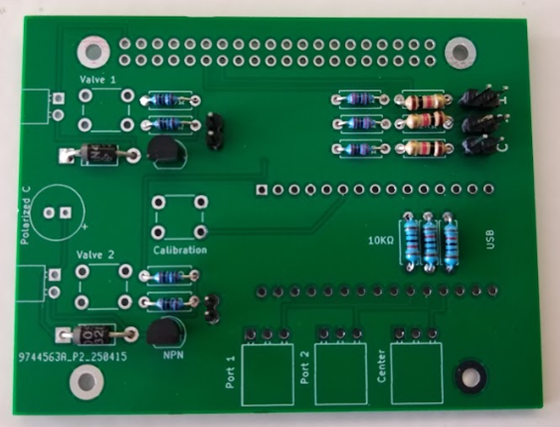
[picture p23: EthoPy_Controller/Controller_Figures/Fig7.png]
  
</figure>

**Step 7**. Solder the tactile push button switch in the appropriate position on the board ([Fig. 8](#fig8)).

<figure id="fig8">
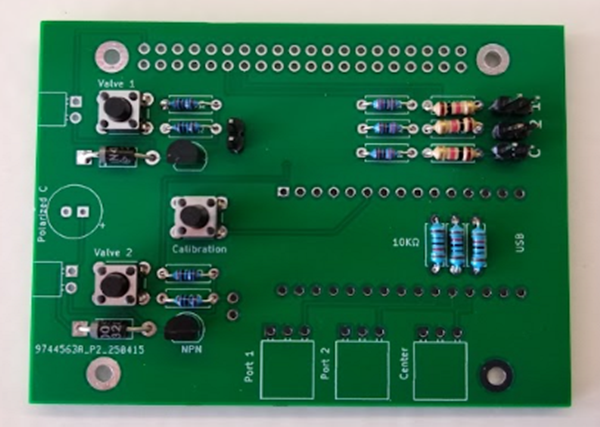
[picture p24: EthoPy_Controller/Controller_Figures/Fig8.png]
  
</figure>

**Step 8**. Solder the capacitor, ensuring the longer positive lead goes into the right hole ([Fig. 9](#fig9)).

<figure id="fig9">
  
</figure>

**Step 9**. Solder the right-angle female pin headers - two on the left side (1x2) for valves and three on the bottom (1x3) for ports and centerport ([Fig. 10](#fig10)).

<figure id="fig10">
  
</figure>

**Step 10**. Solder the two 1x15 female pin headers for the Arduino board ([Fig. 11](#fig11)).

<figure id="fig11">
  
</figure>

**Step 11**. Mount the Arduino board onto the previously mentioned female pin headers ([Fig. 12](#fig12)).

<figure id="fig12">
  
  
</figure>

**Step 12**. Solder the 40-pin extra-tall stackable female header to connect the PCB to the Raspberry Pi board ([Fig. 13](#fig13)).

<figure id="fig13">
  
</figure>

**Step 13**. Set up the Arduino using the code provided [here](). <!--add hyperlink-->

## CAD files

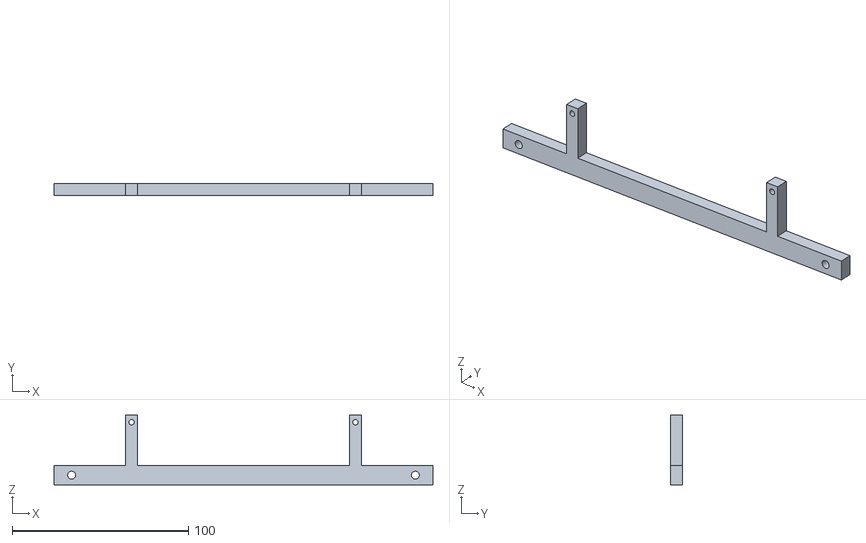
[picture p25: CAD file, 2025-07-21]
Air-track/3d_designs/screen_holder.stl
215.0 x 7.00 x 39.5

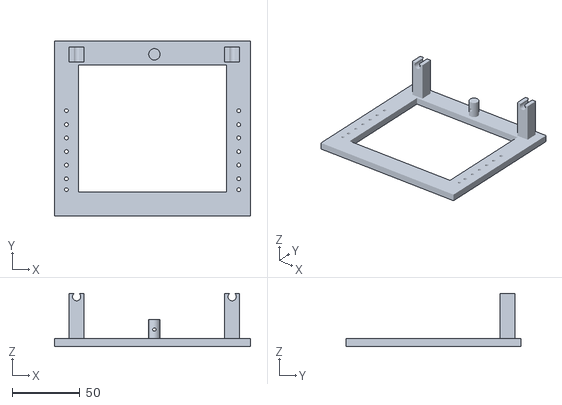
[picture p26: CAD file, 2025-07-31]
Homecage/3d_designs/base.stl
144.2 x 128.7 x 39.0

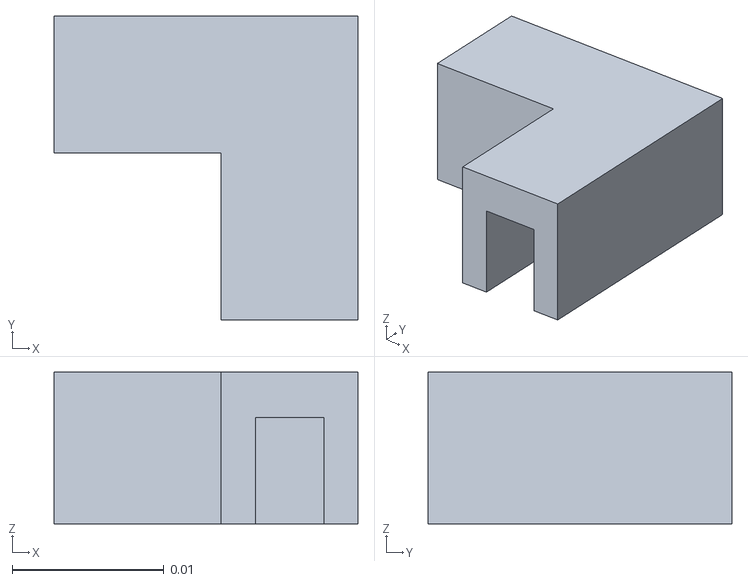
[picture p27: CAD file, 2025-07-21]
Open-field/3d_designs/open-field_top_corner.stl
0.02 x 0.02 x 0.01

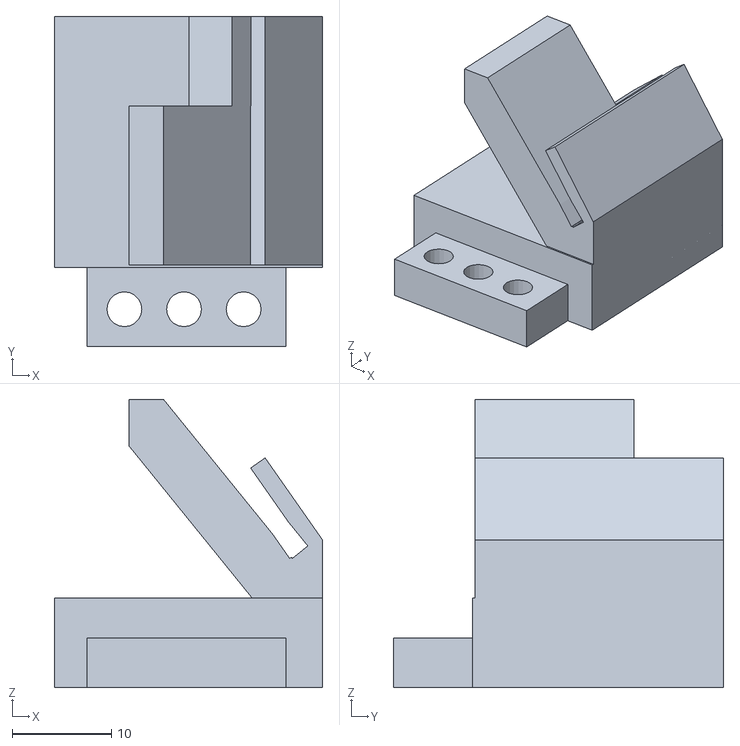
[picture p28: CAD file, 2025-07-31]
Spherical_Treadmill/3d_design/mouse_post.stl
27.0 x 33.2 x 29.0

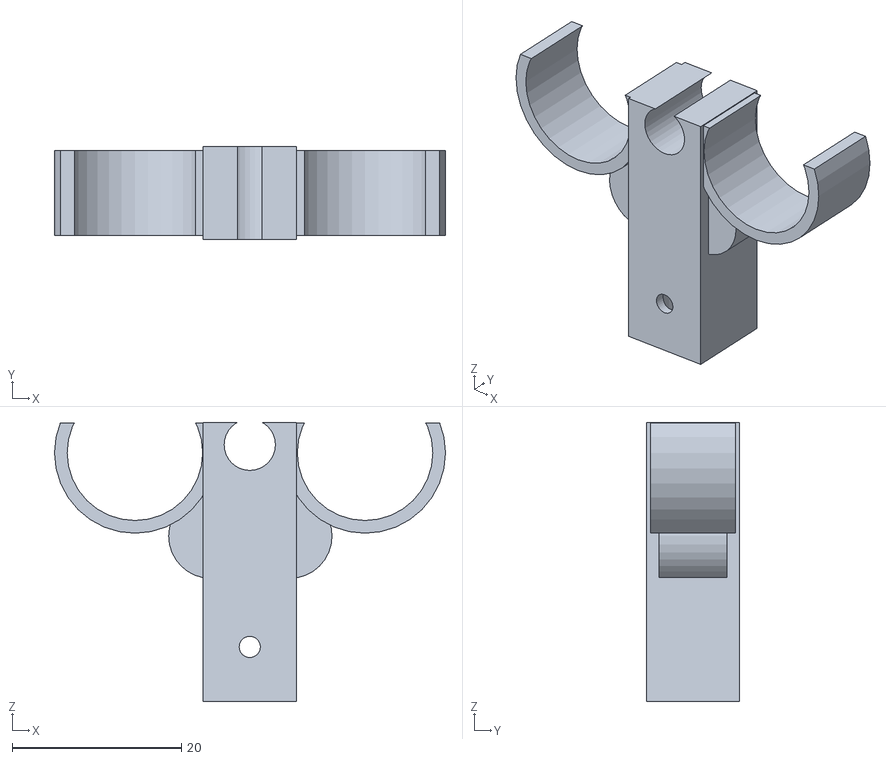
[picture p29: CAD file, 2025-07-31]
Homecage/3d_designs/center_port_with_speakers.stl
46.2 x 11.0 x 33.0

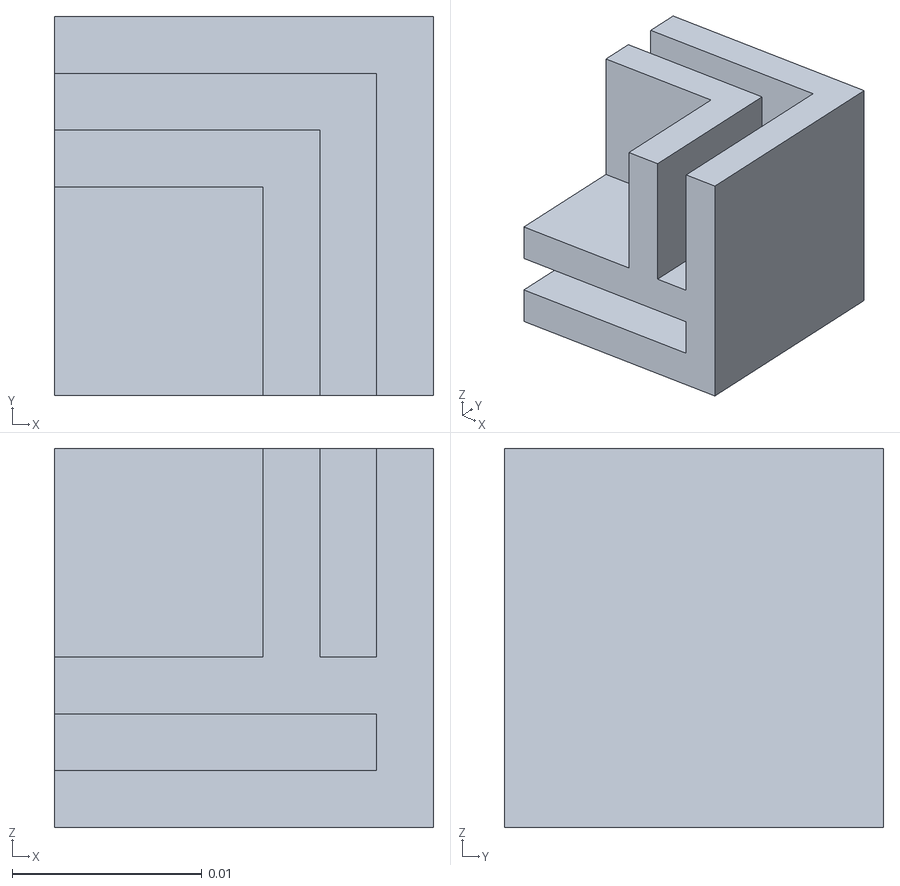
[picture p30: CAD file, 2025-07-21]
Open-field/3d_designs/open-field_bottom_corner.stl
0.02 x 0.02 x 0.02

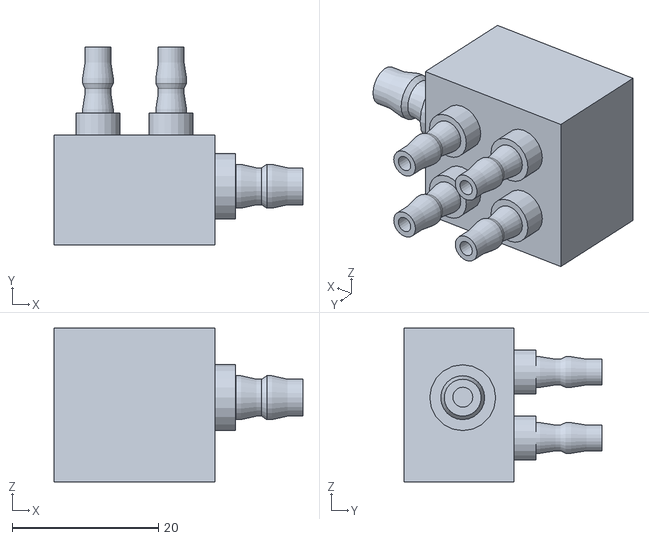
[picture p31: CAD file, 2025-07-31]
Spherical_Treadmill/3d_design/tube_connectors.stl
34.0 x 27.0 x 21.0

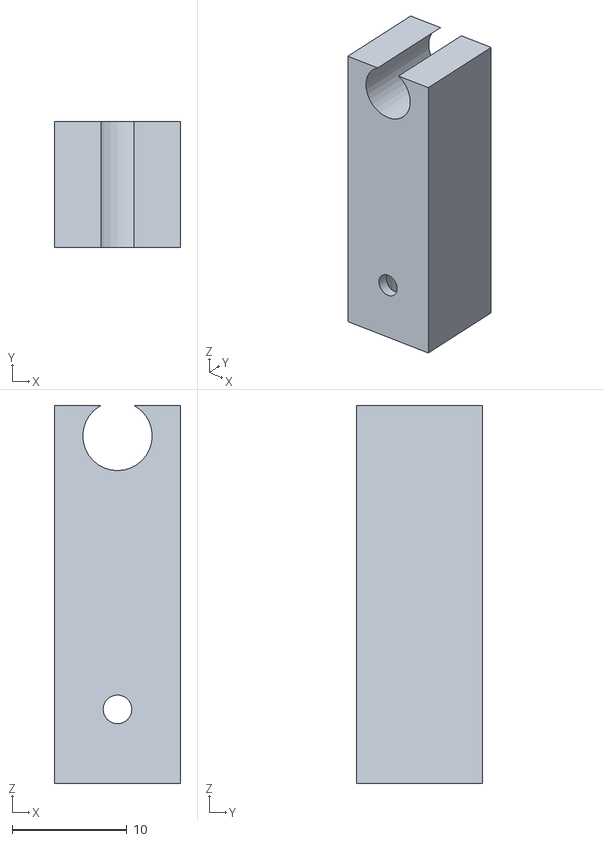
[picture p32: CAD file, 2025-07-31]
Homecage/3d_designs/center_port.stl
11.0 x 11.0 x 33.0

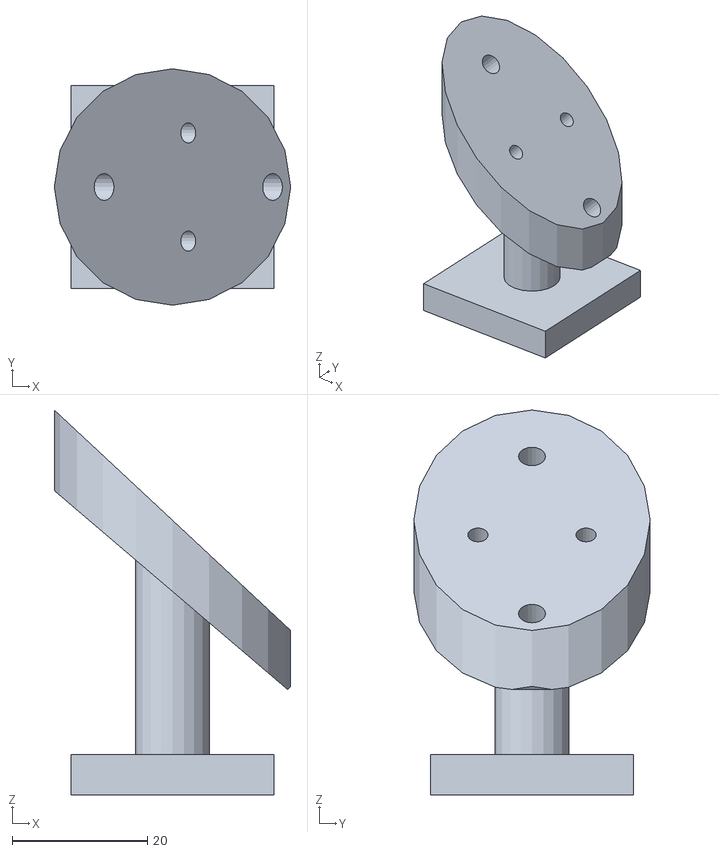
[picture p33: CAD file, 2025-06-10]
Spherical_Treadmill/3d_design/ball-bearing-post.stl
35.0 x 35.0 x 57.0

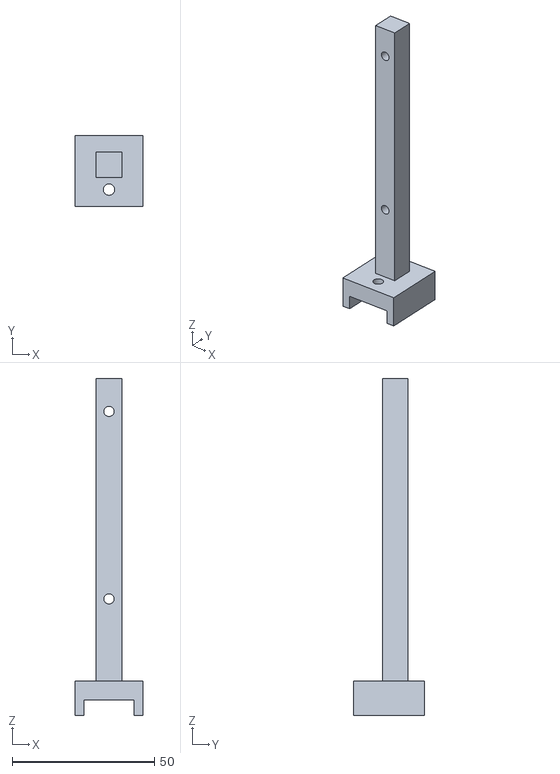
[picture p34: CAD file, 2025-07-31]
Homecage/3d_designs/screen_holder.stl
24.0 x 25.0 x 118.4

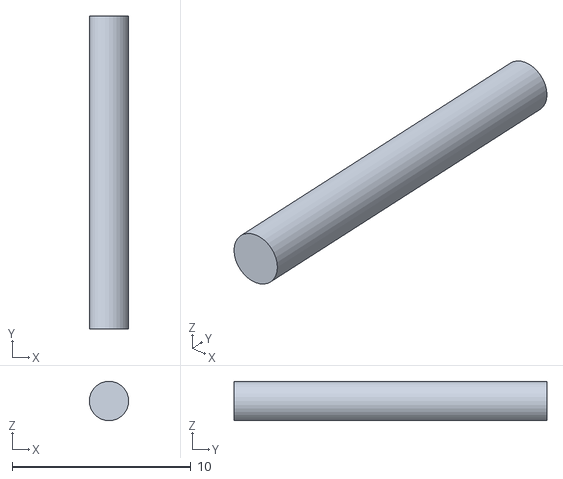
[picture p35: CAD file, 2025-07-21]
Homecage/3d_designs/pin.stl
2.20 x 17.5 x 2.20

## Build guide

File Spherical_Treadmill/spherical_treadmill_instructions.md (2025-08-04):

# Spherical Treadmill Behavioral Setup

The Spherical Treadmill (ball) behavioral setup is used for head-fixed mice performing sensory navigation tasks (e.g., olfactory, visual, multimodal). Below, we describe the protocol to construct an odor-based virtual reality setup. 

## 📦 Hardware Parts List

### 🔌 Electronics

| # | Item                      | Qty  |Source           |Identifier    |  Notes                                 |
|:-:|:-:                        |:-:   |:-:              |:-:           |:-:                                     |

| 1 | solenoid valves           | 5    | fspumb.cn       | 0526T        | 4 for odorants, 1 for water delivery   |

| 2 |MOSFET board               | 5    | OEM             | FR120N       | To control the solenoid valves         |

| 3 | Capacitive sensor board   | 1    | Sparkfun        | AT42QT1011   | for lick detection                     |

| 4 | laser mouse               | 2    | DELL            | MS3220       | ball sensors                           |

| 5 | ball bearings             | 3    | DFRobot         | FIT0007      |                                        |

| 6 | plastic box               | 1    | Kradex          | Z74HJ        | 30 x 20 x 10cm                         |

### 🔧 Other Hardware

| # | Item                      | Qty  |Source           |Identifier    |  Notes                                 |
|:-:|:-:                        |:-:   |:-:              |:-:           |:-:                                     |

| 1 | ball bearings             | 3    | DFRobot         | FIT0007      |                                        |

| 2 | plastic box               | 1    | Kradex          | Z74HJ        | 30 x 20 x 10cm                         |

### 🧩 3D printed parts

You will find the blueprints for the items you should 3D print [here](ethopy_hardware/Homecage/3d_designs).

| # | Item                  | Qty | Filename                                                                        | Notes             |
|:-:|:-:                    |:-:  |:-:                                                                              |:-:                |

| 1 | mouse post            | 2   | [mouse_post.stl](ethopy_hardware/Spherical_Treadmill/3d_design/mouse_post.stl)                 |                   |

| 2 | ball bearing holder   | 3   | [ball_bearing_holder.stl](ethopy_hardware/Spherical_Treadmill/3d_design/ball-bearing-post.stl) |                   |

| 3 | 5-way tube connector  | 1   | [tube_connector.stl](ethopy_hardware/Spherical_Treadmill/3d_design/tube_connector.stl)         |                   |

## 🛠️ Step-by-step assemply instructions

Following instructions apply for any virtual reality system that uses a styrofoam ball on 3 ball bearings (similar to Fig. 4d of the EthoPy paper) <!--Add hyperlink-->, 4 odours to define an olfactory virtual environment, and a mouthpiece to deliver the odors but also the reward.

**Step 1**. Set up the [Raspberry Pi Behavioral Setup](ethopy_hardware/Homecage/RP_instructions.md) following steps 1-5, the difference is that in this setup you need 5 valves ([Electronics parts list, item #1](#electro1)), for reward and 4 for odour delivery. 

**Step 2**. A `Styrofoam ball` is supported by three (3) metallic ball bearings ([Other Hardware parts list, item #1](#other1)) allowing smooth navigation for prolonged periods. The bearings are supported by custom 3D-printed posts ([3D-printed parts, part #2](#printer2)) at a 45° angle, so the ball is stable while the subject is performing the task.

<div align="center">
<figure id="fig1">
  
  <figcaption><b>Figure 1</b>: <i>Animated depiction of the experimental set-up. Mouse is head-fixed onto a styrofoam ball, with a mouthpiece securing the odor and water delivery.</i></figcaption>
</figure>
</div>

**Step 3**. The PCB boards of the laser mice ([Electronics parts list, item #4](#electro4)) are used as sensors to encode the ball movement. Laser mice holders ([3D-printed parts, part #1](#printer1)) are used to place the laser mice in an optimal position at 90⁰ degrees from each other, very close to the bearings, and at an incline of 55°, to eliminate the distance variation between the ball and the sensor that could lead to imprecise tracking information. Insert the PCB board of each laser mouse and ensure they have 2-3 mm distance from the surface of the ball ([Fig. 2](#fig2)).

<div align="center">
<figure id="fig2">
  
  <figcaption><b>Figure 2</b>: <i>Schematic of the locations of the ball bearing holders (grey) and the laser mice (red).</i></figcaption>
</figure>
</div>

> :memo: **Note:** Details about the how EthoPy computes the distances covered by the animal are in [`vr_ball_readme.md`](https://github.com/ef-lab/ethopy_plugins/blob/main/spherical_treadmill/behaviors/vr_ball_readme.md)

**Step 4**. The odor and water delivery system requires constant air supply and 5 solenoid valves. The air supply is connected to a 5-way manifold ([3D-printed parts, part #3](#printer3)) with the 4 valves that open and close when a pulse is sent from the RP through the MOSFET ([Electronics parts list, item #2](#electro2)). Upon pulse delivery the valves open for the specified duration and the air travels through the odor bottle to the mouthpiece. Similarly for the water supply, water is delivered to the lick port inside the mouthpiece upon correct response. 

> :memo: **Note:** Odors are released depending on the animal’s virtual location and are calculated in [`EthoPy Ball`](https://github.com/ef-lab/ethopy_plugins/blob/main/spherical_treadmill/stimuli/vr_odors_readme.md) 

<div align="center">
<figure id="fig3">
  
  <figcaption><b>Figure 3</b>: <i>Animated depiction of the assembly of the stimuli that arrive at the mouthpiece odors (left) and water (right). </i></figcaption>
</figure>
</div>

### ⚡Electrical connections

- `Valves’ control circuit`: To control the valves, we use a MOSFET board ([Electronics parts list, item #2](#electro2)) and connect the power and ground of the valve to the board, placing the power at position 2a and the ground at position 2b shown in [Fig. 4](#fig4). Then, to connect it with the Raspberry Pi, we select the pin of the RP we have programmed to trigger the valve and a ground pin and connect the other end to the PWR and GND pins respectively placed at the top part of the board (position 3, ([Fig. 4](#fig4))). Lastly, to turn on the board we need to insert 2 cables at position 1, one for the power and one for the ground of the power supply. In this last step, it is advised to make a 6-way cable assembly, both for the power and the ground, 5 of them going to each MOSFET board, and one connecting the power supply. This assembly can be placed in a plastic box ([Other Hardware parts list, item #2](#other2)).

<!--add figure 4-->

- `Lick detector circuit`: The Capacitive sensor board ([Electronics parts list, item #3](#electro3)) consists of five pins: GND for ground, OUT for signal, VDD for power supply (1.8V - 5V), LED and PAD ([Fig. 5](#fig5)). In this case, only four of the pins are required (GND, OUT, VDD, and PAD). To connect the sensor for the lick detection it is important to solder a trimmed and polished 18G needle to the wire that will connect with the PAD pin. 

<!--add Figure 5-->

- `Laser mice`: Connect the laser mice to the two USB ports of the RP (each USB port will be assigned later in EthoPy code (Interfaces/Ball.py) to determine which laser mouse is responsible for decoding which axes)

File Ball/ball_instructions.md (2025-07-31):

# Ball Behavioral Setup

The ball behavioral setup is used for head-fixed mice performing sensory navigation tasks (e.g., olfactory, visual, multimodal). Below, we describe the protocol to construct an odor-based virtual reality setup. 

## 📦 Hardware Parts List

### 🔌 Electronics

| # | Item                      | Qty  |Source           |Identifier    |  Notes                                 |
|:-:|:-:                        |:-:   |:-:              |:-:           |:-:                                     |

| 1 | solenoid valves           | 5    | fspumb.cn       | 0526T        | 4 for odorants, 1 for water delivery   |

| 2 |MOSFET board               | 5    | OEM             | FR120N       | To control the solenoid valves         |

| 3 | Capacitive sensor board   | 1    | Sparkfun        | AT42QT1011   | for lick detection                     |

| 4 | laser mouse               | 2    | DELL            | MS3220       | ball sensors                           |

| 5 | ball bearings             | 3    | DFRobot         | FIT0007      |                                        |

| 6 | plastic box               | 1    | Kradex          | Z74HJ        | 30 x 20 x 10cm                         |

### 🔧 Other Hardware

| # | Item                      | Qty  |Source           |Identifier    |  Notes                                 |
|:-:|:-:                        |:-:   |:-:              |:-:           |:-:                                     |

| 1 | ball bearings             | 3    | DFRobot         | FIT0007      |                                        |

| 2 | plastic box               | 1    | Kradex          | Z74HJ        | 30 x 20 x 10cm                         |

### 🧩 3D printed parts

You will find the blueprints for the items you should 3D print [here](ethopy_hardware/Homecage/3d_designs).

| # | Item                  | Qty | Filename                                                                        | Notes             |
|:-:|:-:                    |:-:  |:-:                                                                              |:-:                |

| 1 | mouse post            | 2   | [mouse_post.stl](ethopy_hardware/Ball/3d_design/mouse_post.stl)                 |                   |

| 2 | ball bearing holder   | 3   | [ball_bearing_holder.stl](ethopy_hardware/Ball/3d_design/ball-bearing-post.stl) |                   |

| 3 | 5-way tube connector  | 1   | [tube_connector.stl](ethopy_hardware/Ball/3d_design/tube_connector.stl)         |                   |

## 🛠️ Step-by-step assemply instructions

Following instructions apply for any virtual reality system that uses a styrofoam ball on 3 ball bearings (similar to Fig. 4d of the EthoPy paper) <!--Add hyperlink-->, 4 odours to define an olfactory virtual environment, and a mouthpiece to deliver the odors but also the reward.

**Step 1**. Set up the [Raspberry Pi Behavioral Setup](ethopy_hardware/Homecage/RP_instructions.md) following steps 1-5, the difference is that in this setup you need 5 valves ([Electronics parts list, item #1](#electro1)), for reward and 4 for odour delivery. 

**Step 2**. A `Styrofoam ball` is supported by three (3) metallic ball bearings ([Other Hardware parts list, item #1](#other1)) allowing smooth navigation for prolonged periods. The bearings are supported by custom 3D-printed posts ([3D-printed parts, part #2](#printer2)) at a 45° angle, so the ball is stable while the subject is performing the task.

<div align="center">
<figure id="fig1">
  
  <figcaption><b>Figure 1</b>: <i>Animated depiction of the experimental set-up. Mouse is head-fixed onto a styrofoam ball, with a mouthpiece securing the odor and water delivery.</i></figcaption>
</figure>
</div>

**Step 3**. The PCB boards of the laser mice ([Electronics parts list, item #4](#electro4)) are used as sensors to encode the ball movement. Laser mice holders ([3D-printed parts, part #1](#printer1)) are used to place the laser mice in an optimal position at 90⁰ degrees from each other, very close to the bearings, and at an incline of 55°, to eliminate the distance variation between the ball and the sensor that could lead to imprecise tracking information. Insert the PCB board of each laser mouse and ensure they have 2-3 mm distance from the surface of the ball ([Fig. 2](#fig2)).

<div align="center">
<figure id="fig2">
  
  <figcaption><b>Figure 2</b>: <i>Schematic of the locations of the ball bearing holders (grey) and the laser mice (red).</i></figcaption>
</figure>
</div>

> :memo: **Note:** Details about the how EthoPy computes the distances covered by the animal are in [`vr_ball_readme.md`](https://github.com/ef-lab/ethopy_plugins/blob/main/ball/behaviors/vr_ball_readme.md)

**Step 4**. The odor and water delivery system requires constant air supply and 5 solenoid valves. The air supply is connected to a 5-way manifold ([3D-printed parts, part #3](#printer3)) with the 4 valves that open and close when a pulse is sent from the RP through the MOSFET ([Electronics parts list, item #2](#electro2)). Upon pulse delivery the valves open for the specified duration and the air travels through the odor bottle to the mouthpiece. Similarly for the water supply, water is delivered to the lick port inside the mouthpiece upon correct response. 

> :memo: **Note:** Odors are released depending on the animal’s virtual location and are calculated in [`EthoPy Ball`](https://github.com/ef-lab/ethopy_plugins/blob/main/ball/stimuli/vr_odors_readme.md) 

<div align="center">
<figure id="fig3">
  
  <figcaption><b>Figure 3</b>: <i>Animated depiction of the assembly of the stimuli that arrive at the mouthpiece odors (left) and water (right). </i></figcaption>
</figure>
</div>

### ⚡Electrical connections

- `Valves’ control circuit`: To control the valves, we use a MOSFET board ([Electronics parts list, item #2](#electro2)) and connect the power and ground of the valve to the board, placing the power at position 2a and the ground at position 2b shown in [Fig. 4](#fig4). Then, to connect it with the Raspberry Pi, we select the pin of the RP we have programmed to trigger the valve and a ground pin and connect the other end to the PWR and GND pins respectively placed at the top part of the board (position 3, ([Fig. 4](#fig4))). Lastly, to turn on the board we need to insert 2 cables at position 1, one for the power and one for the ground of the power supply. In this last step, it is advised to make a 6-way cable assembly, both for the power and the ground, 5 of them going to each MOSFET board, and one connecting the power supply. This assembly can be placed in a plastic box ([Other Hardware parts list, item #2](#other2)).

<!--add figure 4-->

- `Lick detector circuit`: The Capacitive sensor board ([Electronics parts list, item #3](#electro3)) consists of five pins: GND for ground, OUT for signal, VDD for power supply (1.8V - 5V), LED and PAD ([Fig. 5](#fig5)). In this case, only four of the pins are required (GND, OUT, VDD, and PAD). To connect the sensor for the lick detection it is important to solder a trimmed and polished 18G needle to the wire that will connect with the PAD pin. 

<!--add Figure 5-->

- `Laser mice`: Connect the laser mice to the two USB ports of the RP (each USB port will be assigned later in EthoPy code (Interfaces/Ball.py) to determine which laser mouse is responsible for decoding which axes)

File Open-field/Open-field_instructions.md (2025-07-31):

# Open-field Behavioral Setup Instructions

In this protocol, the open-field behavioral setup is used to allow freely-moving mice to perform two-alternative forced choice tasks. Below, we describe the protocol to implement an open-field behavioral setup for  a visual discrimination task.

## 📦 Hardware Parts List

### 🔌 Electronics

| # | Item                               | Qty | Source                                   | Identifier                                                   | Notes                                            |
|:-:|:-:                                 |:-:  |:-:                                       |:-:                                                           |:-:                                               |

| 1 | Arduino Nano Every Board           | 1   | Arduino Store                            | ABX00028                                                     |                                                  | 

| 2 | PCB Controller Board               | 1   | JLCPCB (JiaLiChuang (HongKong) Co., LTD) | [custom](ethopy_hardware/Homecage/EthoPy_Controller_Board.md)|  |

| 3 | 13.3" Capacitive Touch Screen LCD  | 1   | Waveshare                                | HDMI LCD (H)                                                 | Presentation of stimuli, with Toughened Glass Cover, 1920×1080 |

| 4 | HDMI Cable (2m, 4K/60Hz)           | 1   | Ugreen                                   |     ED015                                                    |Connects the screen with the PC                    |

### 🔧 Other Hardware

| # | Item                                      | Qty | Source       | Identifier                                                | Notes                                                |
|:-:|:-:                                        |:-:  |:-:           |:-:                                                        |:-:                                                   |

| 1 | V-SLOT 2020 1500mm                        | 1   | Grobotronics | 27-99920208                                               | cut into 4 pieces of 31 cm length                    |

| 2 | V-SLOT 2020 250mm                         | 4   | Grobotronics | 27-99920210                                               |                                                      |

| 3 | V-SLOT 2020 500mm                         | 2   | Grobotronics | 27-99920209                                               |                                                      |

| 4 | Inside Hidden Corner Bracket 3-Way        | 4   | Grobotronics | 14-00015421                                               |                                                      |

| 5 | RatRig Cast - 90 Degree Corner Bracket    | 4   | Grobotronics | 27-22280012                                               |                                                      |

| 6 | Plexiglass Plates                         | 7   | Local vendor | —                                                         | 2 33x33cm plates, 1 30x30cm plate, 4 35x30cm plates  |

| 7 | V-Hive Enclosure Base Model               | 1   | RatRig       | HW3303GK                                                  | Insulation of light and sound                        |

| 8 | ISOLFON Foam Plate                        | —   | Muziker      | —                                                         | Sound insulator                                      |

| 9 | M4 Screws                                 | —   | M4X10        | —                                                         | 11x L10 & 16x L8                                     |

| 10| M4 T-nuts 20x20                           | 9   | _            | 14-00085144                                               |                                                      |

| 11| V-Slot Gantry Set 2020 with Three Wheels  | 2   | Grobotronics | 14-00020155                                               |                                                      |

| 12| Lickport                                  | 1   | _            | [Custom](ethopy_hardware/Homecage/Lick_ports_assemply.md) | Delivers water                                       |

| 13| LHD Series 3-Way Control Solenoid Valve   | 1   | Lee SLR      | LHDA0533415H                                              |                                                      |

### 🧩 3D Printed Parts

| # | Item            | Qty | Filename                                                                                              | Notes |
|:-:|:-:              |:-:  |:-:                                                                                                    |:-:    |
| 1 | Lower Corners   | 4   | [open-field_bottom_corner.stl](ethopy_hardware/Open-field/3d_designs/open-field_bottom_corner.stl)    |       |
| 2 | Upper Corners   | 4   | [open-field_top_corner.stl](ethopy_hardware/Open-field/3d_designs/open-field_top_corner.stl)          |       |

---

## 🛠️ Step-by-step assemply instructions

The open-field behavioral setup is enclosed in the Rat-Rig V-Hive Enclosure Base Model ([Other Hardware list, item #7](#other7)). Assembly instructions can be found here.

### 🔇 Enclosure & Sound Insulation

**Step 1**. To make the enclosure sound-proof, use `sound insulation material` (eg. ISOLFON foam plate, ([Other Hardware list, item #8](#other8))) to cover all sides of the enclosure, i.e. use 4 pieces with dimensions 50x50cm and 2 pieces with dimensions 50x43cm.

### 🐭 Arena Construction

The interior of the enclosure consists of a plexiglass box (arena), where the mouse is placed during the experiment (base: 30x30cm, walls: 35x30 cm, ([Other Hardware list, item #6](#other6))).

**Step 2**. Glue (e.g. hot glue) each side of the arena and place 3D printed parts (3D printed parts list, items #1,2) on the upper and lower corners ([Fig. 1](#fig1)).

<div align="center">
<figure id="fig1">
  
  
  
  <figcaption><b>Figure 1</b>: <i>Open-field arena: the arena (left), the base of the arena (center) and the arena on top of its base and inside the enclosure (right) </i></figcaption>
</figure>
</div>

**Step 3**. Construct the following drawer to place the arena ([Fig. 1](#fig1)).

- `Base`: 4 V-SLOT 2020 ([Other Hardware list, item #1](#other1)) with a length of 31 cm each. Connect the rails in the shape of a square and place a plexiglass (33x33cm, Other Hardware list, item #6) in the middle. When connecting the plexiglass to the square, you need to cut its corners at around 6.1 mm.

- `Columns`: 4 V-SLOT 2020 250 mm ([Other Hardware list, item #2](#other2)). Connect them on the base.

- For the `connections` of the base and columns, use Inside Hidden Corner Brackets and M4 (8mm) screws ([Other Hardware list, item #4,9](#other4,9)).

- `Rails`: 2 V-SLOT 2020 with a length of 50 cm each ([Other Hardware list, item #3](#other3)). Place the rails on the base of the box and screw them using 4 90-Degree Corner Brackets ([Other Hardware list, item #5](#other5)). To screw the brackets on the V-SLOTS, use M4 screws (10mm, ([Other Hardware list, item #9](#other9))) and M4 20x20 Tee Nuts (Other Hardware list, item #10).

- `Sliding`: Screw 2 V-Slot Gantry Sets 2020 with Three Wheels ([Other Hardware list, item #11](#other11)) on each side of the base with M4 (8mm, ([Other Hardware list, item #9](#other9))) screws and M4 20x20 Tee Nuts ([Other Hardware list, item #10](#other10)). Attach each V-Slot Gantry Set to the rails.

### :tv: Screen

**Step 4**. Place a screen ([Electronics list, item #3](#electro3)) on the one side of the box between the 2 V-slots ([Fig. 2](#fig2)).

**Step 5**. Connect the cable for power (included in the 13.3inch Capacitive Touch Screen LCD, ([Electronics list, item #3](#electro3))) and the HDMI ([Electronics list, item #4](#electro4)) ([Fig. 1](#fig1)).

<div align="center">
<figure id="fig2">
  
  
  <figcaption><b>Figure 2</b>: <i>Screen: front side of the screen (left) and back side of the screen and connections (right)</i></figcaption>
</figure>
</div>

### 🧰 Arduino Board

**Step 6**. Follow instructions for [EthoPy Controller Board](ethopy_hardware/Homecage/Ethopy_Controller_Board.md)

### 💧 Lickport

**Step 7**. Follow instructions [here](ethopy_hardware/Homecage/Lick_ports_assemply.md) to make the lickport ([Other Hardware list, item #12](#other12)).

**Step 8**. Connect the lickport to the arduino board and a solenoid valve ([Other Hardware list, item #13](#other13)) in a pressurized tubing network (STAR methods, liquid delivery).

### ⚙️ Extra parts

To record the experiment you need red LED lights :rotating_light: and a camera :camera:

> :bulb: **Note:** We used Arducam 2.3MP AR0234 Color Global Shutter USB 3.0 Camera Module-With Enclosure. If you use a camera that records in darkness, lights might not be necessary.

### 🖥️ PC requirements
For the Open-field setup in the EthoPy project, in addition to the standard installation, you will need to enable real-time pose estimation by installing `DeepLabCut-Live`, which provides a lightweight, low-latency inference pipeline for online tracking. To achieve frame rates greater than 30 FPS, we strongly recommend using a system running Ubuntu paired with a powerful NVIDIA GPU (minimum 8GB VRAM), as this ensures compatibility with TensorFlow and allows for GPU-accelerated inference. CPU-only systems or unsupported GPUs (e.g., Intel or AMD) will not meet the real-time demands.

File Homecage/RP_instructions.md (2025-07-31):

# Raspberry Pi Behavioral Setup
A key component of multiple Ethopy behavioral systems is the [Raspberry Pi](https://www.raspberrypi.com/), a small, affordable, single-board computer. It includes ports for HDMI, USB, Ethernet, audio, camera interface (CSI), display interface (DSI), and General Purpose Input/Output (GPIO) pins. It primarily runs on a Linux-based OS called Raspberry Pi OS, and also supports other operating systems. Below, we analytically describe the steps to implement a Raspberry Pi-based behavioral setup.

<div align="center">
  <figure id="fig1">
    
  </figure>
</div>

## 📦 Hardware Parts List

### 🔌 Electronics

| # | Item                                          | Qty     | Source              | Identifier            | Notes                                                                                     |
|:-:|:-:                                            |:-:      |:-:                  |:-:                    |:-:                                                                                        |

| 1 | Raspberry Pi 4 Model B/4GB                    | 1       | Raspberry Pi             |SC0192-3|                                                                                           |

| 2 | Official Raspberry Pi 7 Touch Screen Display  | 1       | Raspberry Pi              |  2473872         |                                                                                           |

| 3 | Premium High Speed microSD Card               | 1       |  Integral  | INMSDH32G-100/70V30              |                                                                                           |

| 4 | EthoPy Controller Board                       | 1       | [Custom](ethopy_hardware/Homecage/EthoPy_Controller_Board.md)              |                       |                                                                                           |

| 5 | Lick Ports                                    | 2 or 3  | [Custom](ethopy_hardware/Homecage/Lick_ports_assemply.md)              |                       | 2 to detect licks and deliver water, 1 can be used as a proximity indicator (center port) |

| 6 | Beam Photoelectric Sensor                     | 1       | HAITRONIC               | HR0172          |Can be used as a proximity indicator (center port)                                         |

| 7 | Solenoid valves                               | 2       | LEE SLR         | LHDA0533415H               |                                                                                           | <!--Verify Mfr. source-->

| 8 | Ultrasound Speakers 40kHz                     | 2       | PUI Audio      | UT-1640K-TT-2-R    |For auditory experiments. See: [Speakers_assemply](ethopy_hardware/Homecage/Speakers_assemply.md)                                                                    |

### 🔧 Other Hardware

| # | Item                                | Qty | Source      | Identifier    | Notes       |
|:-:|:-:                                  |:-:  |:-:          |:-:            |:-:          |

| 1 | M3 screws                           | 6   | Grobotronics  | M3X12/D7985  |             | <!--Verify Mfr. source & Identifier-->

| 2 | Raspberry Pi 4 Heatsink (40x30x5mm) | 1   | Grobotronics  | 49-00012076  |             | <!--Verify Mfr. source & Identifier-->

### 🧩 3D printed parts
You will find the blueprints for the items you should 3D print [here](ethopy_hardware/Homecage/3d_designs).
| # | Item                          | Qty | Filename                                                                                            | Notes                           |
|:-:|:-:                            |:-:  |:-:                                                                                                  |:-:                              |
| 1 | Base                          | 1   | [base.stl](ethopy_hardware/Homecage/3d_designs/base.stl)                                            | Includes the lick port holders  |
| 2 | Screen holder                 | 2   | [screen_holder.stl](ethopy_hardware/Homecage/3d_designs/screen_holder.stl)                          |                                 |
| 3 | Center port holder            | 1   | [center_port.stl](ethopy_hardware/Homecage/3d_designs/center_port.stl)                              |                                 |
| 4 | Center port & speaker holder  | 1   | [center_port_with_speakers.stl](ethopy_hardware/Homecage/3d_designs/center_port_with_speakers.stl)  | Includes speaker holders        |
| 5 | Pins                          | 1   | [pin.stl](ethopy_hardware/Homecage/3d_designs/pin.stl)                                              | For mounting the center port holder |

<figure id="fig1">
  
  
  <figcaption><b>Figure 1</b>: <i>RP setup (top: 3D printed parts of the RP’s base, bottom: assembled RP base).</i></figcaption>
</figure>

## 🛠️ Step-by-step assemply instructions

**Step 1**. Install the [operating system of the RPi](https://www.raspberrypi.com/documentation/computers/getting-started.html#installing-the-operating-system). In our experiments, we have used the [Bullseye Raspberry Pi OS](https://www.raspberrypi.com/news/raspberry-pi-os-debian-bullseye/).

**Step 2**. Mount the Raspberry Pi to the Raspberry Pi Touch Display and connect the Flat Flexible Cable and the power of the Touch Display to the Raspberry Pi [instructions](https://www.raspberrypi.com/documentation/accessories/display.html).

**Step 3**. Connect the Ethopy Controller Board to the RPi.

**Step 4**. Add a heatsink ([Other Hardware parts list, item #2](#other2)) on the back of the RP to avoid excessive warming.

**Step 5**. Plug in the side and the center ([lick](ethopy_hardware/Homecage/Lick_ports_assemply.md) or interruptor) ports, and the valves to the EthoPy Controller Board, to the positions indicated on the board.

**Step 6**. Connect the valves to the water supply. Each LEE valve ([Electronics parts list, item #7](#electro7)) has 3 pipe-edges (1) to be connected to the lick port tube, (2) to be connected with the water supply tube, and (3) to be connected with the other valve through a tube and 2 pins to be connected to the board ([Fig. 2, left](#fig1)).

In the RP setup, the upper valve corresponds to the left lick port, and the bottom valve corresponds to the right lick port ([Fig. 2, right](#fig1)).

<figure id="fig2">
  
  
  <figcaption><b>Figure 2</b>: <i>Connections of the solenoid valve (left: positions of the tubes, right: placement of the valves on the RP board).</i></figcaption>
</figure>

**Step 7**. Connect to the RPi and run a test task.

- ssh username@ip_address 

> For more information, visit their: [Rasberry Pi: Remote access](https://www.raspberrypi.com/documentation/computers/remote-access.html)

- Follow the instructions on how to [install/run EthoPy](https://ef-lab.github.io/ethopy_package/installation/)

> :memo: **Note (Optional):** Rename the RP and set a static IP address.

> :bulb: **Tip:** When using multiple RPs, it is best to use unique names that follow a consistent structure and assign static IP addresses to each RP to facilitate identification and management. To do this, connect to the RP and change its default name following the [instructions](https://ef-lab.github.io/ethopy_package/raspberry_pi). It is recommended to use a fixed prefix followed by an incremental number for each RP added.

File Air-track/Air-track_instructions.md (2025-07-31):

# Air-track setup

In this paradigm, head-fixed mice perform a visual two-alternative forced choice task. This setup can be adapted to accommodate more sensory modalities by using appropriate equipment.

## 📦 Hardware parts list

### 🔌 Electronics

| # |Item                                                         |Qty  |Source                 |Identifier   |Notes                          |
|:-:|:-:                                                          |:-:  |:-:                    |:-:          |:-:                            |

|1  |Bpod port interface board                                    |3    |Sanworks               |1008         |Controlling the behavior ports |

|2  |solenoid valves                                              |2    |LEE                    |LHDA0533415H |                               |

|3  |Infrared Emitter 880nm Circular Right Angle 2-Pin Side Looker|3    |Honeywell              |SEP8736-002  |For the behavior ports         |

|4  |Phototransistor IR Chip Silicon 880nm 2-Pin Side Looker      |3    |Honeywell              |SDP8436-002  |For the behavior ports         |

|5  |Ethernet cable                                               |3    |Bel                    |BC-5UK005F   |                               |

|6  |Cable 0.05 mm², Ø 0.8mm                                      |1    |TRU_                   |1567774      |                               |

### 🔧 Other Hardware

| # |Item                                                           |Qty                                  |Source                 |Identifier   |Notes                          |
|:-:|:-:                                                            |:-:                                  |:-:                    |:-:          |:-:                            |

|1  |Plexiglas air-table                                            |1                                    |Provided by Mostafa A. Nashaat, Larkum Lab, Larkum Lab, Charite, Berlin|             |

|2  |PLA platform                                                   |1                                    |Provided by Mostafa A. Nashaat, Larkum Lab, Charite, Berlin          |             |

|3  |Behavior port                                                  |3                                    |                       |             |                               |

|4  |Crimp For Dupont Female                                        |15                                   |Ninigi                 |NDR-T        |                               |

|5  |Tygon S3™ E-3603 Tubing (water) Ø Inner 2.38mm, Ø outer 3.97mm |4 pieces                             |Optubus                |TY2,38ST3,97 |                               |

|6  |Tygon S3™ E-3603 Tubing (water) Ø Inner 0.79mm, Ø outer 2.38mm |2 pieces                             |Optubus                |TY0,79ST2,38 |                               |

|7  |V-Hive Enclosure Base Model                                    |1                                    |RatRig                 |HW3303GK      |                               |

|8  |Sound insulator ISOLFON foam plate                             |4 pieces 50x50cm and 2 pieces 50x43cm|Mega Acoustic          |244317 (PA-PMP5-DG-5050)      |for sound and light insulation |

|9  |Heat shrink set                                                |                                     |GROBOTRONICS           |05-00017098  |                               |

### 🧩 3D printed parts

You will find the blueprints for the items you should 3D print [here](ethopy_hardware/Air-track/3d_designs).

| # |Item                                                           |Qty  |Filename                                                                         |
|:-:|:-:                                                            |:-:  |:-:                                                                              |
|1  |screen holders                                                 |2    |[screen_holder.stl](ethopy_hardware/Air-track/3d_designs/screen_holder.stl) |

## 🛠️ Step-by-step assembly instructions

You will find the blueprints for the items you should 3D print [here](3d_designs).

> :bulb: **Info:** The  air-table ([see Other Hardware, part #1](#hardware1)) and platform ([see Other Hardware, part #2](#hardware2)) of the air-track were developed by Dr. Mostafa A. Nashat and assembly (https://doi.org/10.1152/jn.00088.2016, https://doi.org/10.1101/2024.08.22.608577).

**Step 1**. Set up the [Raspberry Pi Behavioral Setup](ethopy_hardware/Homecage/RP_instructions.md) following steps 1-7, modifying Raspberry Pi Behavioral Setup Step 5 to connect only the valves ([see Electronics, part #2](#electro2)) to the EthoPy Controller Board.

**Step 2**. Mount the Raspberry Pi Behavioral Setup on the screen holders ([see 3D printed parts, part #1](#printed1)) in front of the air-table ([Fig. 1](#fig1)).

<figure id="fig1">
  
  
  <figcaption><i>Figure 1: The RP behavioral setup, mounted on the aluminum rails of the air-table using the screen holders.</i></figcaption>
</figure>

**Step 3**. Assembling of a behavior port ([see Other Hardware, part #3](#hardware3)). Mounting of the infrared emitter ([see Electronics, part #3](#electro3)) and phototransistor ([see Electronics, part #4](#electro4)) to the port was performed following the instructions provided [here](https://sanworks.github.io/Bpod_Wiki/assembly/mouse-behavior-port-assembly/). Each platform included three behavior ports.

> :memo: **Note:** For our experiments, we did not include LED light in the behavior ports. 

**Step 4**. Set up three Bpod port interface boards ([see Electronics, part #1](#electro1)) as per instructions provided [here](https://sanworks.github.io/Bpod_Wiki/assembly/port-breakout-board-assembly/). Place the Bpod port Interface Boards close to the Air-track and the Raspberry Pi Behavioral Setup for convenience.

**Step  5**. For each port, connect the infrared emitter and phototransistor with the Bpod port interface board.

> :memo: **Note:** To reduce the tension caused to the platform from these connections, prefer using wires with a cross-section of 0.05 mm² and an outer diameter of 0.8 mm ([see Electronics, part #6](#electro6)).

**Step 6**. Connecting the Bpod port interface boards to the Raspberry Pi Behavioral Setup. As the connections with the Bpod port interface board are through an Ethernet cable, you will need 3 Ethernet cables, one per port ([see Electronics, part #5](#electro5)).

**Step 7**. Remove the insulation from the edge of the Ethernet wires. Place 13 female terminals ([see Other Hardware, part #4](#hardware4)) at the end of each wire and cover the exposed terminal with insulation (e.g., heat shrink tube, [see Other Hardware, part #9](#hardware9)). In the following steps, the identification of the Ethernet cable wires is shown in ([Fig. 2](#fig2)).

<figure id="fig2">
  
  <figcaption><i>Figure 2: Ethernet cable wire number ids.</i></figcaption>
</figure>

> :memo: **Note:** You will use the wires 1 (signal of the sensor), 4 (power of the emitter), 5 (ground).

**Step 8**.  The wires from the Ethernet cables are connected to the Raspberry Pi Behavioral Setup (see GPIO connections as set in [EthoPy documentation](https://ef-lab.github.io/ethopy_package/local_conf/?h=channel#4-schema-names-optional)) as follows:

- Connect `wire 1` (signal) of each Ethernet cable to the <ins>respective GPIO pin</ins> for the proximity input of each port.
- Connect `wire 4` (power) of each Ethernet cable to a <ins>5V power pin</ins>.
- Connect `wire 5` (ground) of each Ethernet cable to a <ins>ground pin</ins>.

> :memo: **Note:**  Power cables and grounds should be short-circuited together to connect to one pin of the Raspberry Pi.

**Step 9**. Driving of the valves for ports 1 and 2 using the [`EthoPy Controller Board`](ethopy_hardware/Homecage/EthoPy_Controller_Board.md).

**Step 10**. Adjust the reward tubes ([see Other Hardware, part #5](#hardware5), [part #6](#hardware6)) to the behavioral port and connect the valves. Bridge the valves and connect to the water supply ([Fig. 3](#fig3)).

<figure id="fig3">
  
  <figcaption><i>Figure 3: Solenoid valve with the positions of the tubes</i></figcaption>
</figure>

**Step 11**. If sound/light insulation is needed, the Air-track behavioral system can be enclosed in the [`Rat-Rig V-Hive Enclosure Base Model`](https://ratrig.dozuki.com/Guide/01.+V-Hive+Enclosure+Base+Model/183?lang=en) ([see Other Hardware, part #7](#hardware7)). For further sound and light insulation, related insulation material (e.g. ISOLFON foam plate, see ([see Other Hardware, part #8](#hardware8))) can be used to cover the sides of the enclosure.

**Step 12**. The behavioral system should be placed in a room with `air supply`, needed for the floating of the platform on the air-table and the water delivery.

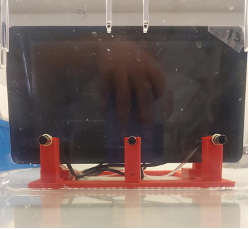
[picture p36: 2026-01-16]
Homecage/Cage_modification_Figures/figure_step7a.png

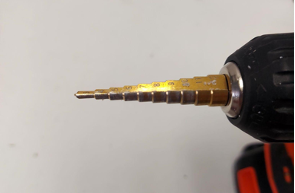
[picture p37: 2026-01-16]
Homecage/Cage_modification_Figures/figure_step6.png

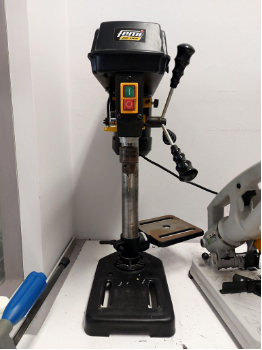
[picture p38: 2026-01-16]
Homecage/Cage_modification_Figures/figure_step4.png

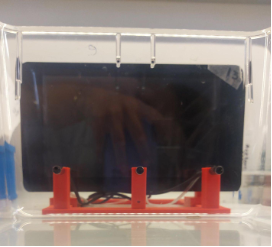
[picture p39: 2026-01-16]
Homecage/Cage_modification_Figures/figure_step2b.png

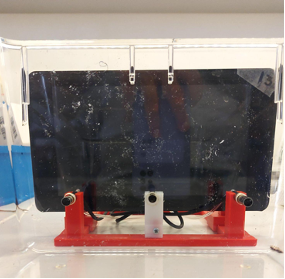
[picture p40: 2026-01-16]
Homecage/Cage_modification_Figures/figure_step8a.png

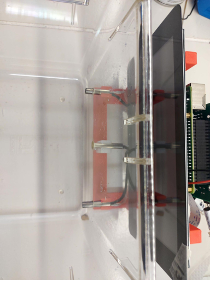
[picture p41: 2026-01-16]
Homecage/Cage_modification_Figures/figure_step8b.png

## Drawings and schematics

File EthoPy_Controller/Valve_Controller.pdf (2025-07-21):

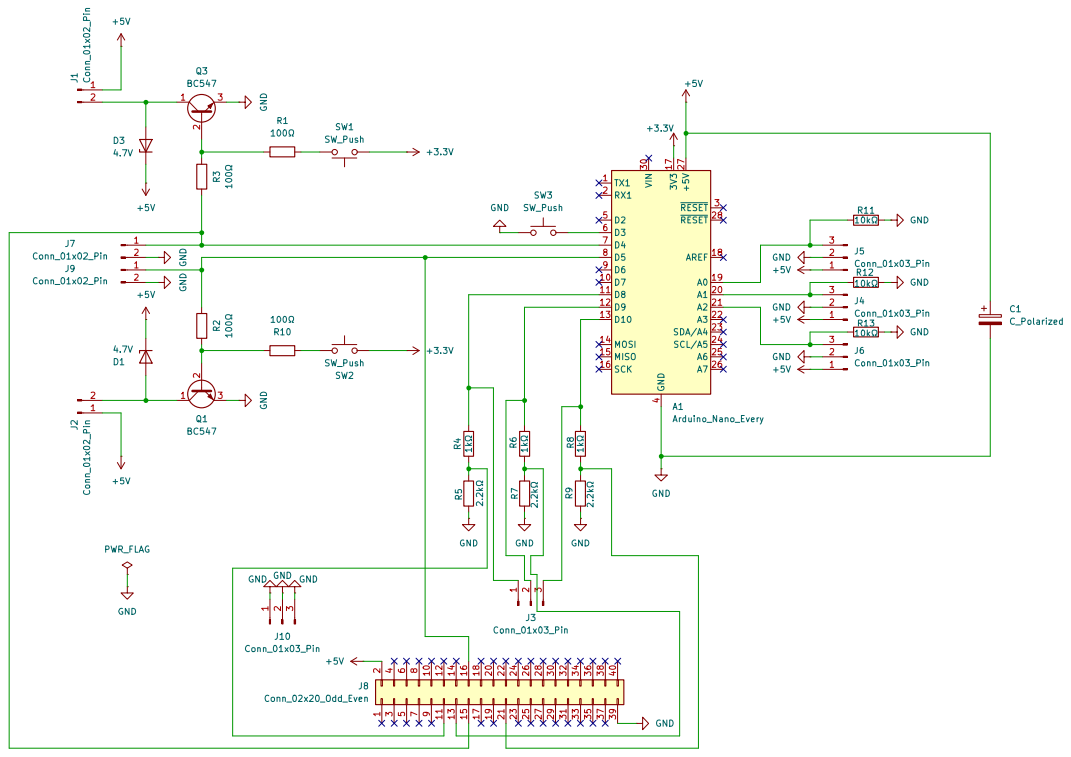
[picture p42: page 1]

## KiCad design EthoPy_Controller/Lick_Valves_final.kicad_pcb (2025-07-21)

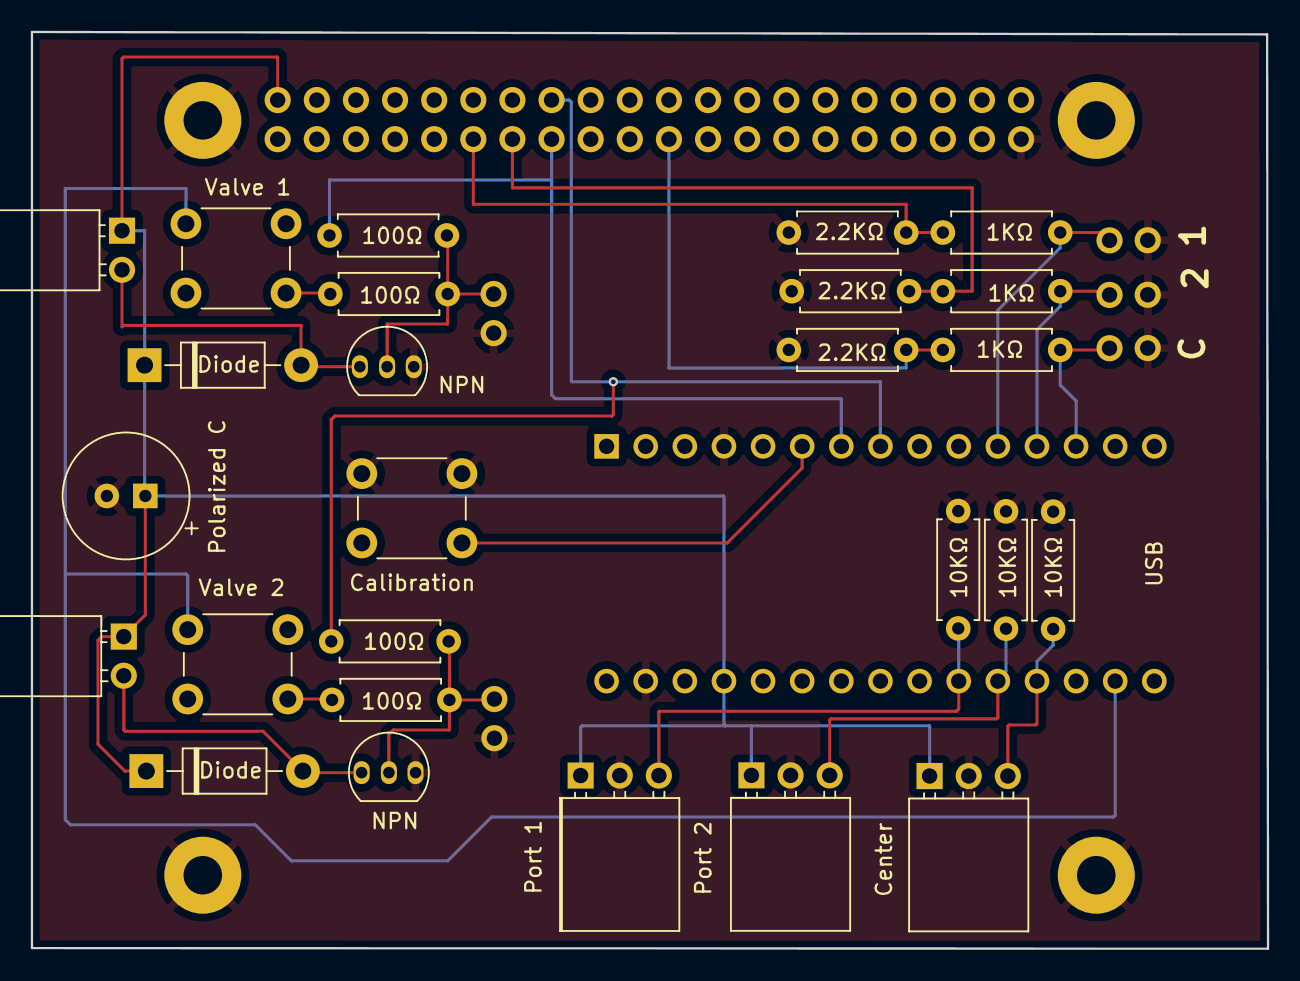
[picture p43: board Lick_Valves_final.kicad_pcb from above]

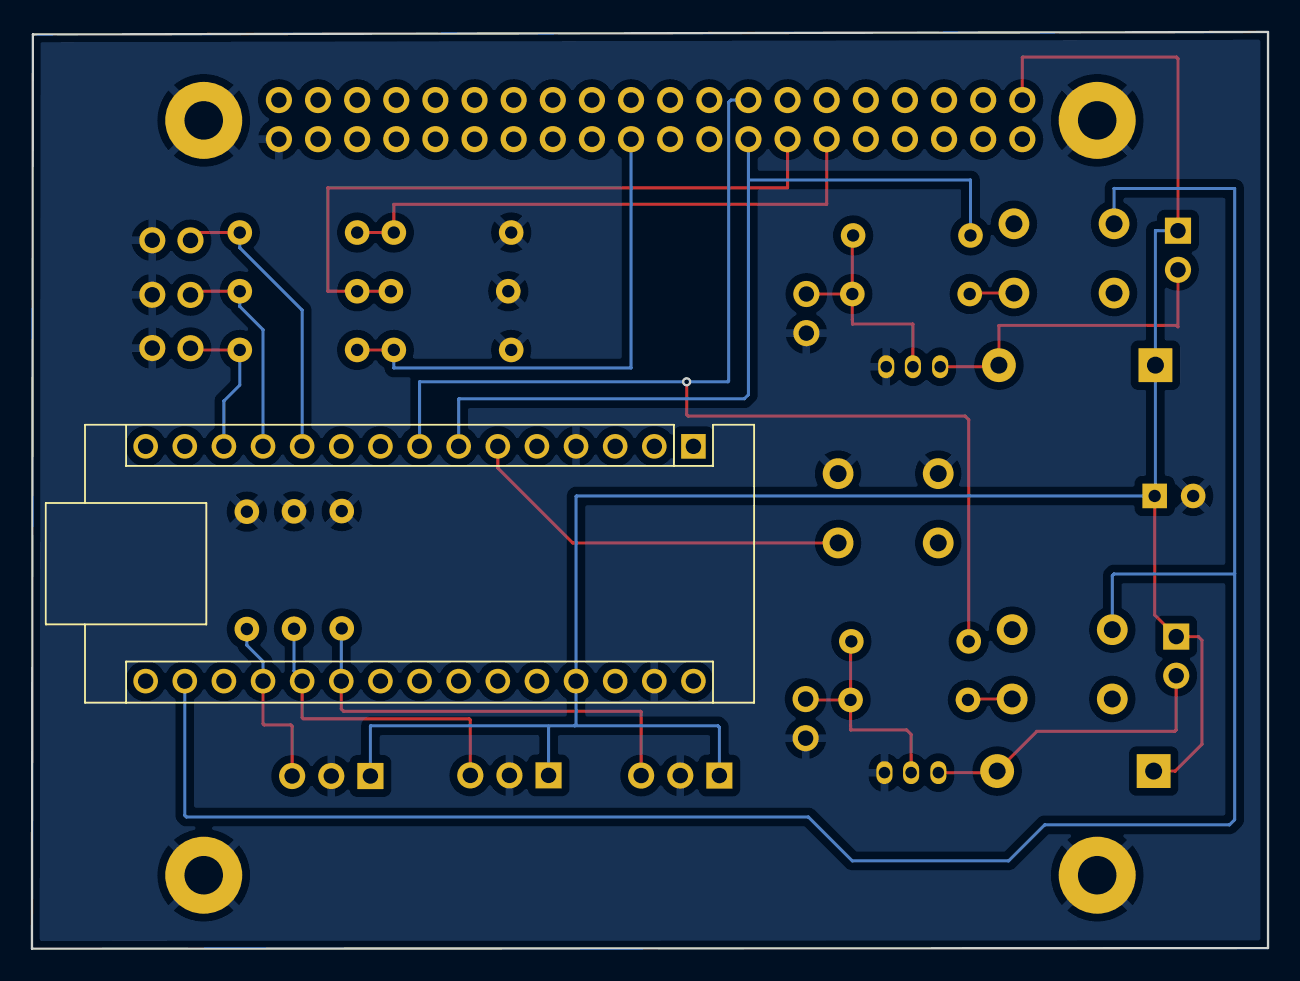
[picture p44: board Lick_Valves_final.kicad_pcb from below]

Board: 4 copper layers, 80.2 x 59.5 mm, 32 parts (2 on the bottom side), 21 nets.

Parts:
A1: Arduino_Nano_Every; Arduino_Nano
C1: C_Polarized; CP_Radial_D8.0mm_P2.50mm
D1, D3: 4.7V; D_DO-41_SOD81_P10.16mm_Horizontal
J1, J2: Conn_01x02_Pin; PinSocket_1x02_P2.54mm_Horizontal
J3, J10: Conn_01x03_Pin; PinHeader_1x03_P2.54mm_Vertical
J4, J5, J6: Conn_01x03_Pin; PinSocket_1x03_P2.54mm_Horizontal
J7, J9: Conn_01x02_Pin; PinHeader_1x02_P2.54mm_Vertical
J8: Conn_02x20_Odd_Even; PinSocket_2x20_P2.54mm_Vertical
Q1, Q3: BC547; TO-92_Inline
R1, R2, R3, R10: 100Ω; R_Axial_DIN0207_L6.3mm_D2.5mm_P7.62mm_Horizontal
R4, R6, R8: 1kΩ; R_Axial_DIN0207_L6.3mm_D2.5mm_P7.62mm_Horizontal
R5, R7, R9: 2.2ΚΩ; R_Axial_DIN0207_L6.3mm_D2.5mm_P7.62mm_Horizontal
R11: 10kΩ; R_Axial_DIN0207_L6.3mm_D2.5mm_P7.62mm_Horizontal
R12, R13: 10ΚΩ; R_Axial_DIN0207_L6.3mm_D2.5mm_P7.62mm_Horizontal
SW1, SW2: SW_Push; SW_PUSH_6mm
SW3: Calibration; SW_PUSH_6mm

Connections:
+3.3V: A1.17 (3V3), SW1.1, SW2.1
+5V: A1.27 (+5V), C1.1, D1.1 (K), D3.1 (K), J1.1, J2.1, J4.1, J5.1, J6.1, J8.2
GND: A1.4 (GND), A1.29 (GND), C1.2, J4.2, J5.2, J6.2, J7.1, J8.39, J9.1, J10.1, J10.2, J10.3, Q1.3 (E), Q3.3 (E), R5.1, R7.1, R9.1, R11.1, R12.1, R13.1, SW3.1
unnamed: A1.19 (A0), J5.3, R11.2
unnamed: A1.20 (A1), J4.3, R12.2
unnamed: A1.21 (A2), J6.3, R13.2
unnamed: A1.6 (D3), SW3.2
unnamed: A1.7 (D4), J8.15, R3.1
unnamed: A1.8 (D5), J8.16, R2.1
unnamed: A1.11 (D8), J3.1, R4.2
unnamed: A1.12 (D9), J3.2, R6.2
unnamed: A1.13 (D10), J3.3, R8.2
unnamed: D1.2 (A), J2.2, Q1.1 (C)
unnamed: D3.2 (A), J1.2, Q3.1 (C)
unnamed: J8.11, R4.1, R5.2
unnamed: J8.13, R6.1, R7.2
unnamed: J8.21, R8.1, R9.2
unnamed: J9.2, Q1.2 (B), R2.2, R10.1
unnamed: J7.2, Q3.2 (B), R1.1, R3.2
unnamed: R1.2, SW1.2
unnamed: R10.2, SW2.2

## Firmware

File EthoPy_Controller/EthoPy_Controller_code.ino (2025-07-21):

#include <EEPROM.h>

int mx_center;
int mx_lick_1;
int mx_lick_2;
bool low_center = false;
bool low_lick_1 = false;
bool low_lick_2 = false;
int CenterInput;
int LickInput1;
int LickInput2;
int v;
int LickPin1 = 8;  // output Port 1
int LickPin2 = 9;  // output Port 2
int CenterPin = 10;  // output Center Port 
int LiquidPin1 = 4;  // input Port 1
int LiquidPin2 = 5;  // input Port 2
int interruptPin = 3; // interrupt pin

void setup() {
  // Get stored thresholds
  mx_lick_1 = readIntFromEEPROM(0);
  mx_lick_2 = readIntFromEEPROM(2);
  mx_center = readIntFromEEPROM(4);

  // Setup inpup/output pins
  pinMode(interruptPin, INPUT_PULLUP);  // sets interrupt pin
  pinMode(LickPin1, OUTPUT);  // sets the pin as output Port 1
  pinMode(LickPin2, OUTPUT);  // sets the pin as output Port 2
  pinMode(CenterPin, OUTPUT);  // sets the pin as output Port Center
  pinMode(LiquidPin1, INPUT);  // sets the pin as input Port 1
  pinMode(LiquidPin2, INPUT);  // sets the pin as input Port 2
}

void loop() {
  // if interrupt, calibrate
  if (digitalRead(interruptPin) == LOW) {
    calibrate();
  }

  // Read analog values
  CenterInput = analogRead(A0);
  LickInput1 = analogRead(A2);
  LickInput2 = analogRead(A1);

  // Compare to stored thresholds
  low_lick_1 = LickInput1 > mx_lick_1;
  low_lick_2 = LickInput2 > mx_lick_2;
  low_center = CenterInput > mx_center;

  // Write digita outputs
  digitalWrite(LickPin1, low_lick_1);
  digitalWrite(LickPin2, low_lick_2);
  digitalWrite(CenterPin, low_center);
}

void calibrate() {
  // read max values to calibrate
  v =  analogRead(A2);
  writeIntIntoEEPROM(0, v);
  v =  analogRead(A1);
  writeIntIntoEEPROM(2, v);
  v =  analogRead(A0);
  writeIntIntoEEPROM(4, v);

  // Get stored thresholds
  mx_lick_1 = readIntFromEEPROM(0);
  mx_lick_2 = readIntFromEEPROM(2);
  mx_center = readIntFromEEPROM(4);
}

void writeIntIntoEEPROM(int address, int number) { 
  EEPROM.put(address, number >> 8);
  EEPROM.put(address + 1, number & 0xFF);
}

int readIntFromEEPROM(int address) {
  return (EEPROM.read(address) << 8) + EEPROM.read(address + 1);
}

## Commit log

2025-04-16 add 3d designs for homecage setup
    [base.stl, center_port.stl, lick_port.stl, screen_stand.stl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]
2025-06-10 update folder structure and add VR files
    [VR_Parts_list.xlsx, ball_bearing_holder.stl, base.stl, center_port.stl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]
2025-07-21 add board pdf test
2025-07-21 upload pdfs fot homecage
    [base.stl, center_port.stl, center_port_with_speakers.stl, pin.stl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]
2025-07-21 upload pdfs fot homecage and delete old files
    [lick_port.stl, screen_stand.stl, speaker_hold.stl]
2025-07-21 update folder name
    [base.stl, center_port.stl, center_port_with_speakers.stl, pin.stl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]
2025-07-21 add air-trck files
    [screenholder_v4.stl]
2025-07-21 add openfield files
    [open-field_bottom_corner.stl, open-field_top_corner.stl]
2025-07-21 remove vr
    [VR_Parts_list.xlsx, ball_bearing_holder.stl, mouse_and_ball_holder.stl, odor_holder.stl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]
2025-07-21 add ehtopy controller design files and code
    [Lick_Valves_final-B_Mask.gbs, Lick_Valves_final-B_Paste.gbp, Lick_Valves_final-B_Silkscreen.gbo, Lick_Valves_final-Back.gbl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]
2025-07-31 Upload markdown file for Homecage hardware
    [base.stl, center_port.stl, center_port_with_speakers.stl, screen_holder.stl]
2025-07-31 Style: Update md & add hyperlinks
    [screen_holder.stl]
2025-07-31 Upload Ball hardware
    [ball-bearing-post.stl, mouse_post.stl, tube_connectors.stl]
